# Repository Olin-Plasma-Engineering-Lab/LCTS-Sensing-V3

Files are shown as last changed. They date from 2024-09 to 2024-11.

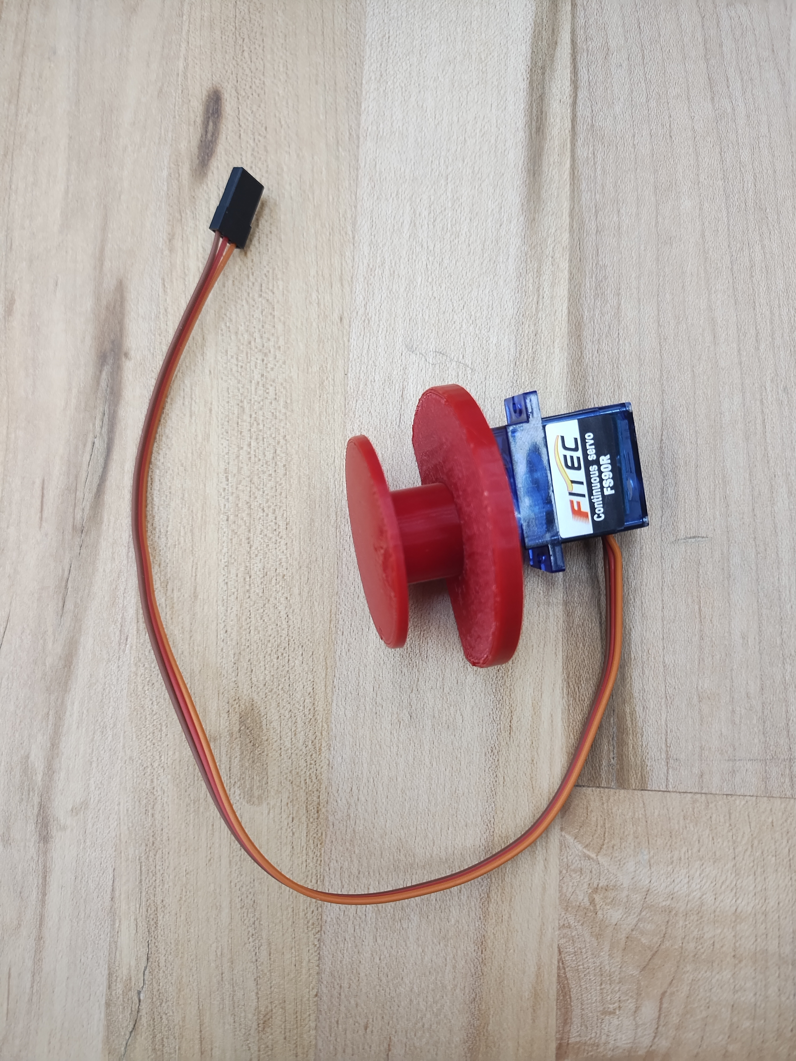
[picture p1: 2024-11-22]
assets/calibration servo.jpg

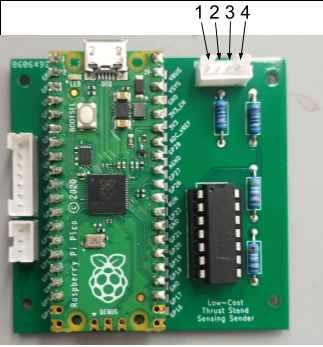
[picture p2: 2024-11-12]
assets/annotated force pinout sender.png

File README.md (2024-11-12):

# LCTS-Sensing-V3

This is the repository for the sensing system used by the Olin Plasma Engineering Lab (OPEL) to measure thrust on the Low-Cost Thrust Stand.

## Brief System Overview
The system is comprised of two boards: a sender and a receiver. The sender is located in the vacuum chamber and is connected to a force sensor that measures thrust produced by the thrusters. The receiver board is located outside the vacuum chamber and exists to receive data sent by the sender board. The boards are connected via a wiring harness and electrical feedthrough on the vacuum chamber, and communicate using I2C.

The system allows for two way communication. This gets used so that the calibration system on the thrust stand within the vacuum chamber can be controlled using the receiver board outside the chamber.

## Repository Organization

- `code/`: This contains the code used by the systems
    - `Microcontroller/`: Code that gets uploaded to the microcontrollers
        - `Arduino/`: Arduino code that gets uploaded to the microcontrollers
            - `receiver/`: code for the receiver board
            - `sender/` (depreicated): code for the sender board for use with **STEPPER MOTOR CALIBRATION**
            - `sender_servo_calibration/`: code for the sender board for use with **SERVO MOTOR CALIBRATION** This is the most up to date script and the code that is actually used on the sender board
        - `Micropython/`: Location for future microcontroller code written in MicroPython. Not currently used but contains the MicroPython firmware
- `Testing/`: Contain a Python script that was used as a preliminary test for saving data to a CSV
- `data/`: Data recorded from unlabeled thruster tests
- `Hardware/`: KiCad projects and other needed files for the sender and receiver PCBs
    - `assets/`: OPEL logo for use on PCBs
    - `Parts/`: Parts needed fro the KiCad Project files
    - `receiver/`: KiCad project files for the receiver PCB
    - `sender/`: KiCad project files for the sender PCB
- `sensing_processor.py`: Script that is used to read data from the receiver and save to a CSV
    
##

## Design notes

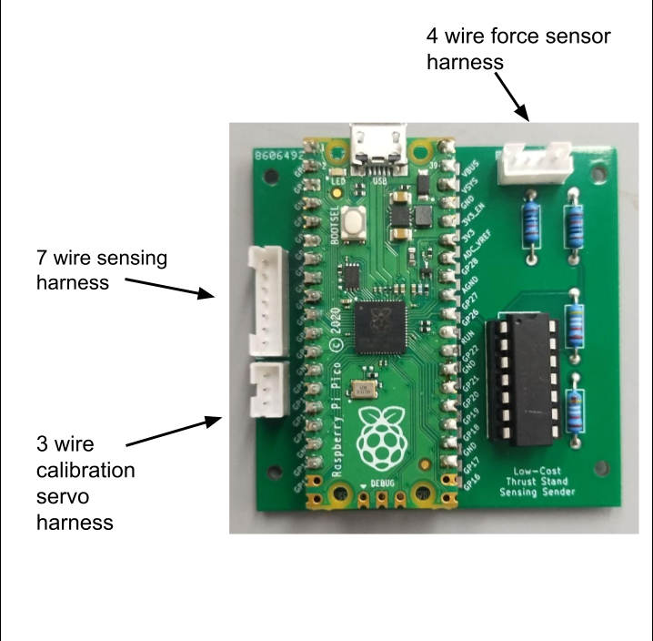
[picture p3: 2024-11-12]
assets/annotated_sender.png

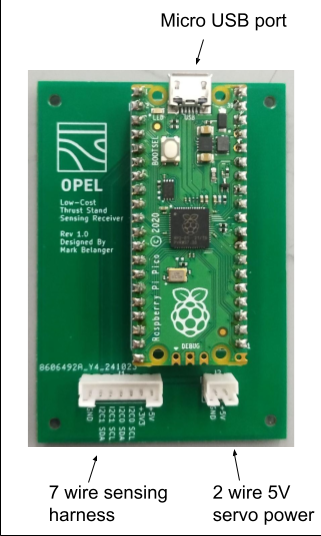
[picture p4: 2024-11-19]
assets/annotated harness receiver.png

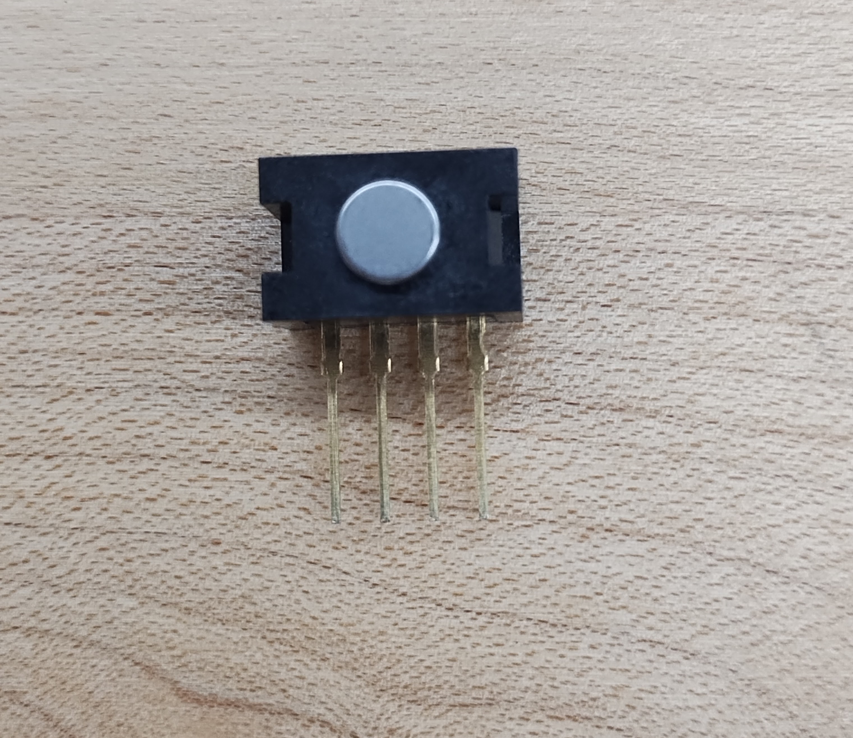
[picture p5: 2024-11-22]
assets/force sensor.jpg

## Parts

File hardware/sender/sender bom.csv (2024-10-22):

Id | Designator | Footprint | Quantity | Designation | Supplier and ref
1 | R2 | R_0603_1608Metric | 2 | 50k
2 | U3 | DIP254P762X508-14 | 1 | LMC6484IN_NOPB
3 | J1 | JST_PH_B7B-PH-K_1x07_P2.00mm_Vertical | 1 | Conn_01x07_Socket
4 | J3 | JST_PH_B3B-PH-K_1x03_P2.00mm_Vertical | 1 | Conn_01x03_Socket
5 | R1 | R_0603_1608Metric | 2 | 10k
6 | U4 | RPi_Pico_SMD_TH | 1 | Pico
7 | J2 | JST_PH_B4B-PH-K_1x04_P2.00mm_Vertical | 1 | Conn_01x04_Socket
8 | R4 | R_0603_1608Metric | 2 | 50k
9 | R3 | R_0603_1608Metric | 2 | 10k

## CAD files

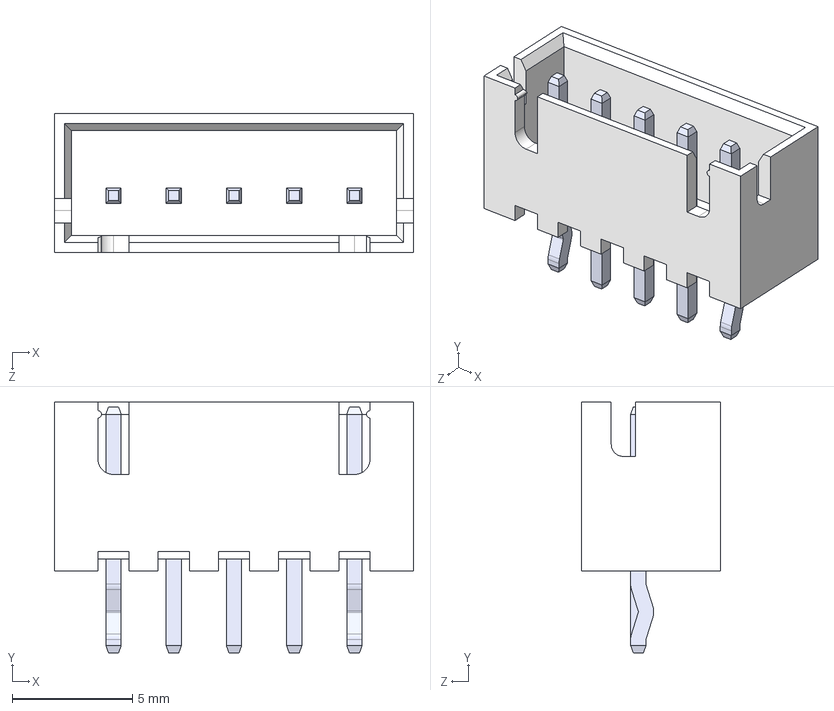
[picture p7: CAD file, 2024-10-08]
hardware/Parts/B5B_XH_A/B5B-XH-A.step
14.9 x 10.4 x 5.75 mm

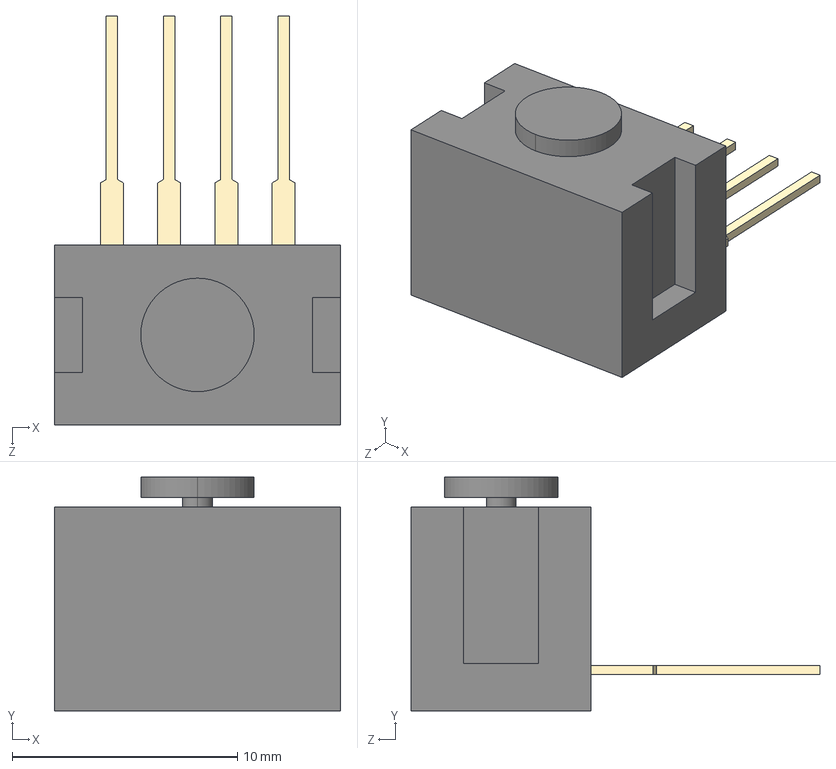
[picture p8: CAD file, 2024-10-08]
hardware/Parts/LIB_FSG005WNPB/3D/FSG005WNPB.stp
12.7 x 10.4 x 18.1 mm

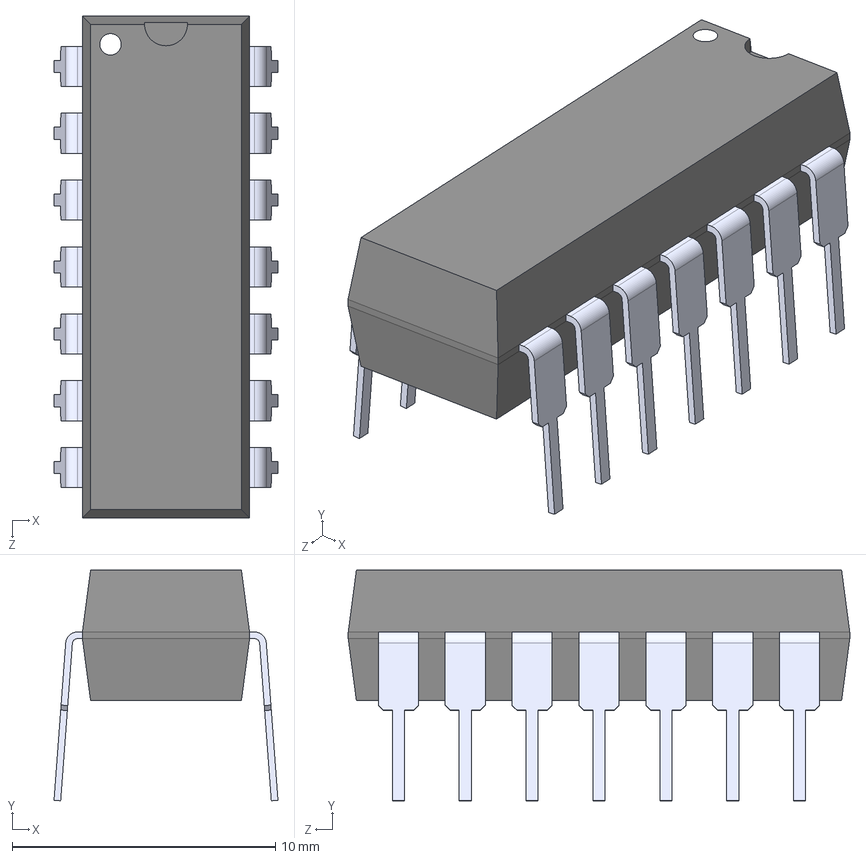
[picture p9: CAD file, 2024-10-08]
hardware/Parts/LMC6484IN_NOPB/LMC6484IN_NOPB.step
8.51 x 8.76 x 19.1 mm

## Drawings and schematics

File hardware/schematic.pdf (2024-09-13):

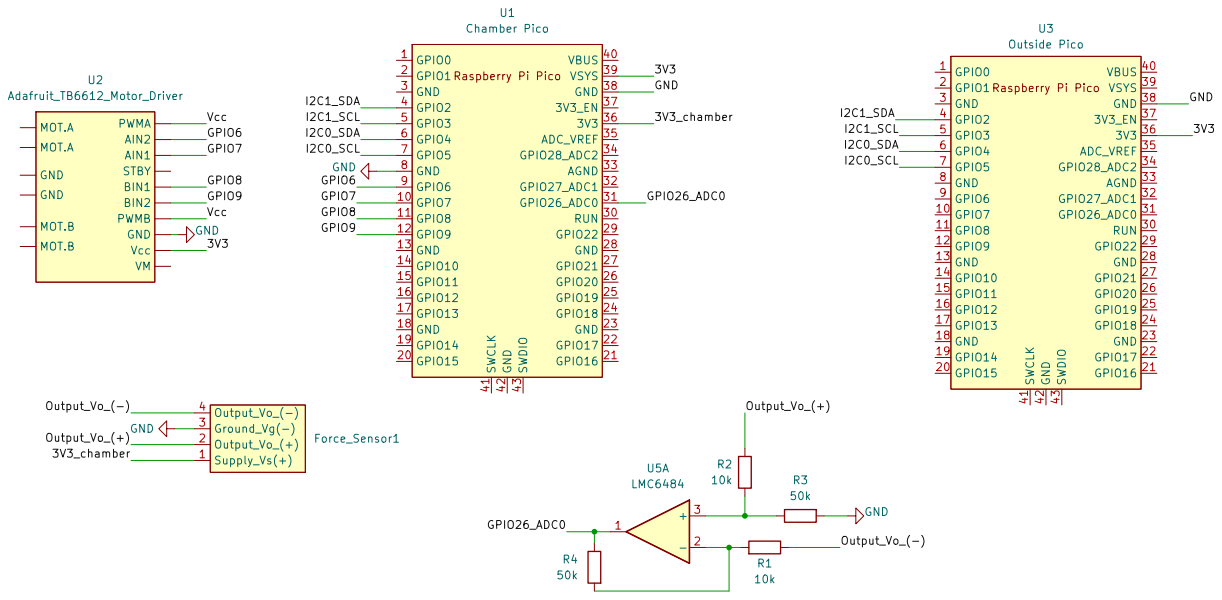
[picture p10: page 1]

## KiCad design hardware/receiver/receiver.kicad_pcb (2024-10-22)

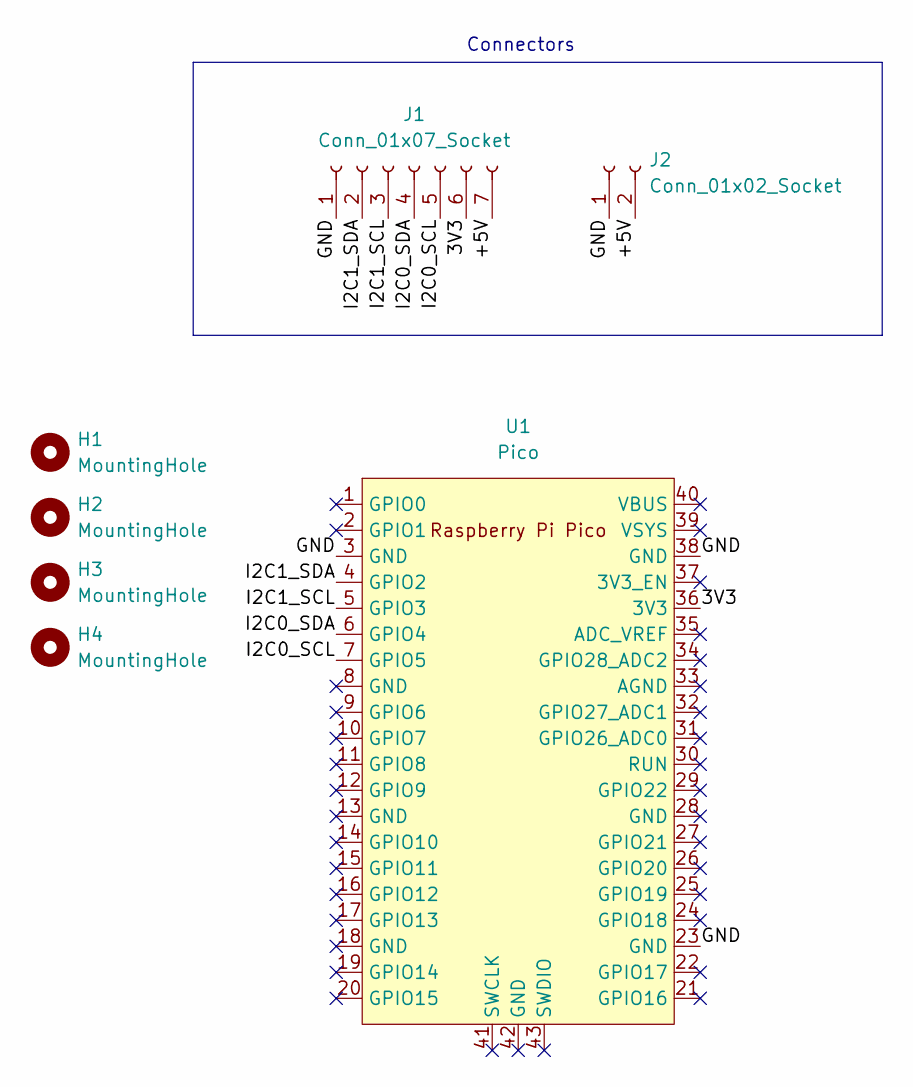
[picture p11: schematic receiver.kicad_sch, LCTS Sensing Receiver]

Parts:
H1, H2, H3, H4: MountingHole; MountingHole_2.2mm_M2
J1: Conn_01x07_Socket; JST_PH_B7B-PH-K_1x07_P2.00mm_Vertical
J2: Conn_01x02_Socket; JST_PH_B2B-PH-K_1x02_P2.00mm_Vertical
U1: Pico; RaspberryPi_Pico_Common_THT

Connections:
/3V3: J1.6, U1.36 (3V3)
/+5V: J1.7, J2.2
/GND: J1.1, J2.1, U1.3 (GND), U1.23 (GND), U1.38 (GND)
/I2C0_SCL: J1.5, U1.7 (GPIO5)
/I2C0_SDA: J1.4, U1.6 (GPIO4)
/I2C1_SCL: J1.3, U1.5 (GPIO3)
/I2C1_SDA: J1.2, U1.4 (GPIO2)

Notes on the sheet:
Connectors

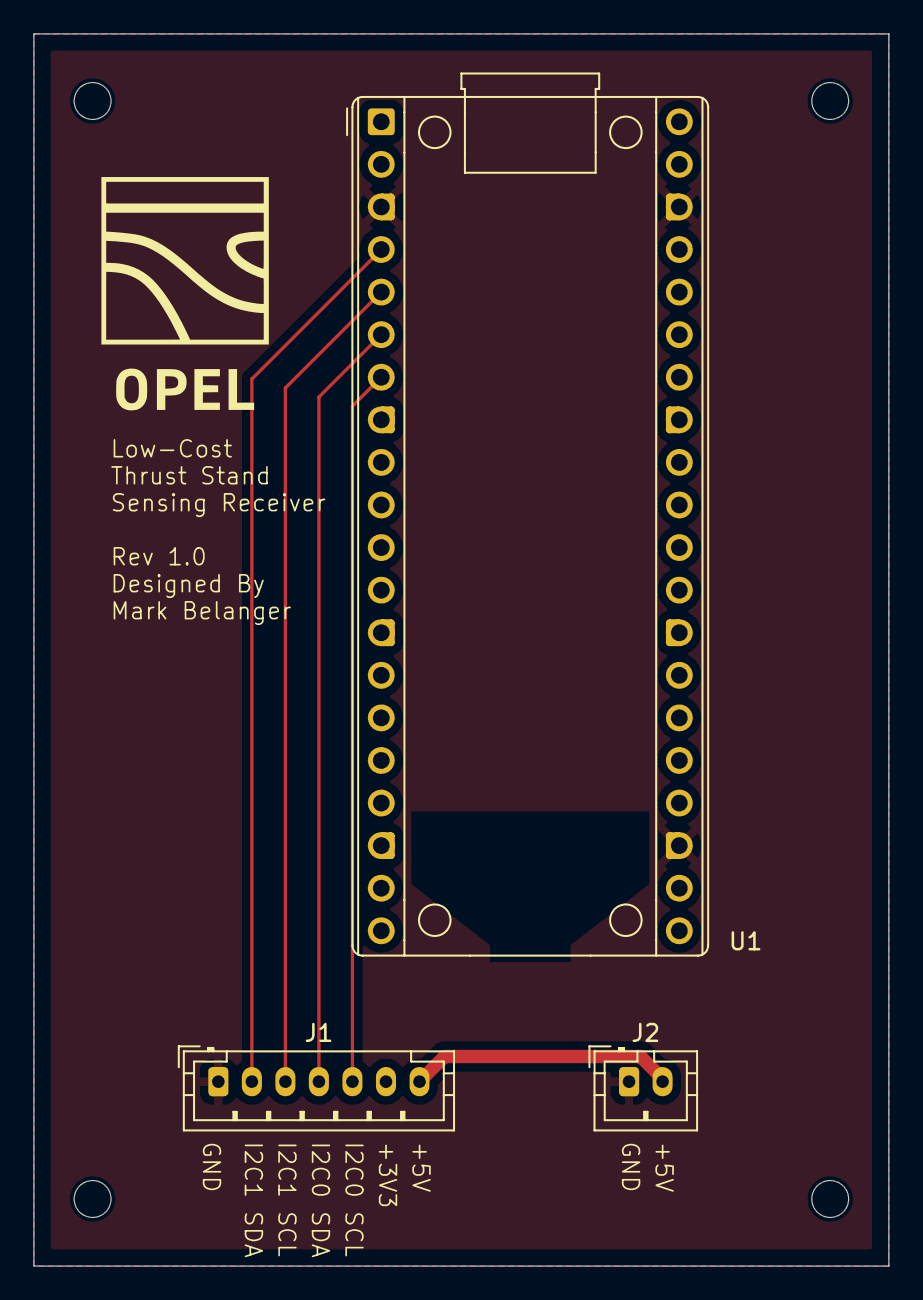
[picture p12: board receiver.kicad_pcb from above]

Board: 2 copper layers, 51.0 x 73.5 mm, 7 parts (0 on the bottom side), 7 nets.

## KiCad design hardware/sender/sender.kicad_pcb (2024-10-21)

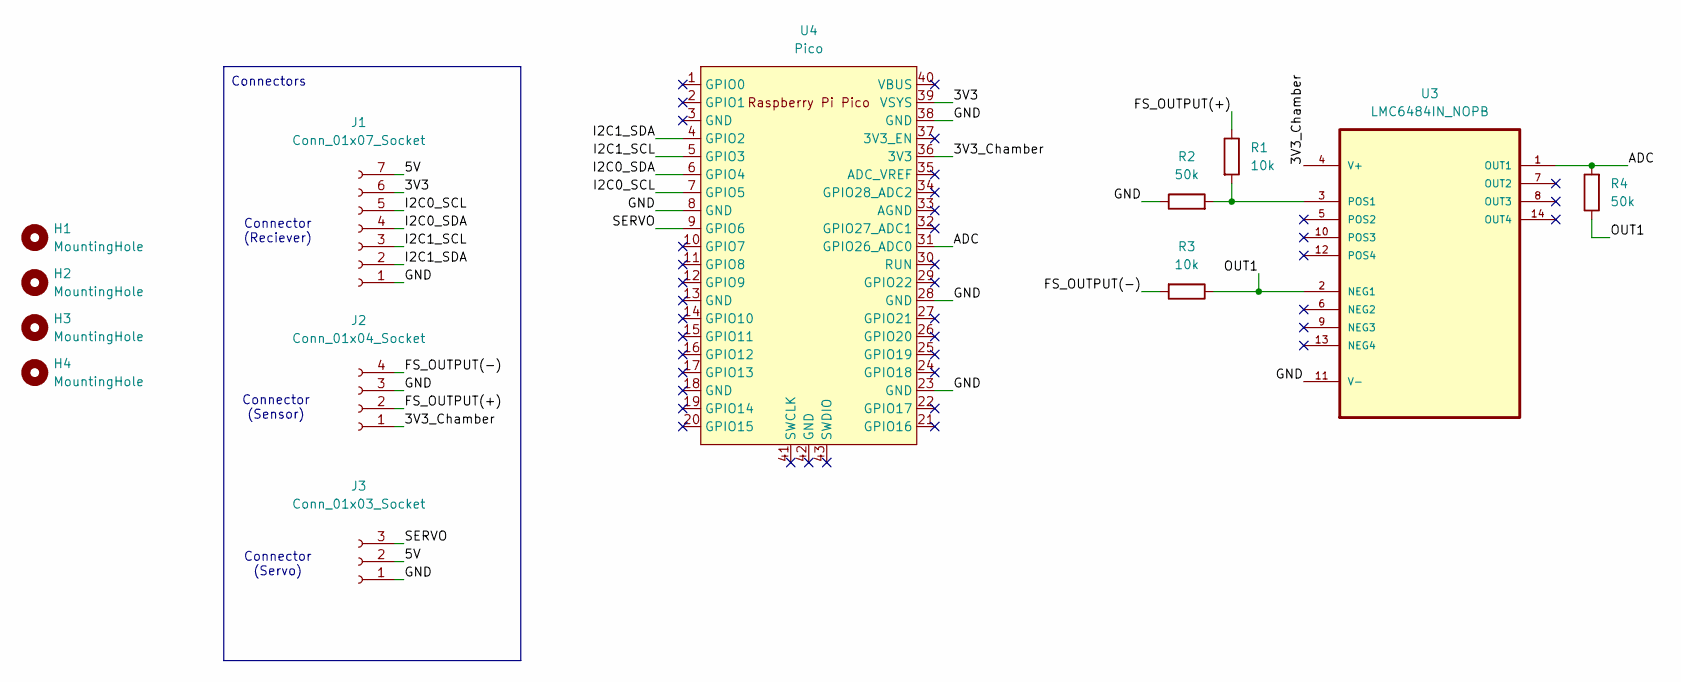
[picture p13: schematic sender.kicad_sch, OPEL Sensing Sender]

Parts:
H1, H2, H3, H4: MountingHole; MountingHole_2.2mm_M2
J1: Conn_01x07_Socket; JST_PH_B7B-PH-K_1x07_P2.00mm_Vertical
J2: Conn_01x04_Socket; JST_PH_B4B-PH-K_1x04_P2.00mm_Vertical
J3: Conn_01x03_Socket; JST_PH_B3B-PH-K_1x03_P2.00mm_Vertical
R1, R3: 10k; R_0603_1608Metric
R2, R4: 50k; R_0603_1608Metric
U3: LMC6484IN_NOPB; DIP254P762X508-14; MPN LMC6484IN/NOPB
U4: Pico; RPi_Pico_SMD_TH

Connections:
/3V3: J1.6, U4.39 (VSYS)
/3V3_Chamber: J2.1, U3.4 (V+), U4.36 (3V3)
/5V: J1.7, J3.2
/ADC: R4.2, U3.1 (OUT1), U4.31 (GPIO26_ADC0)
/FS_OUTPUT(+): J2.2, R1.1
/FS_OUTPUT(-): J2.4, R3.2
/GND: J1.1, J2.3, J3.1, R2.1, U3.11 (V-), U4.8 (GND), U4.23 (GND), U4.28 (GND), U4.38 (GND)
/I2C0_SCL: J1.5, U4.7 (GPIO5)
/I2C0_SDA: J1.4, U4.6 (GPIO4)
/I2C1_SCL: J1.3, U4.5 (GPIO3)
/I2C1_SDA: J1.2, U4.4 (GPIO2)
/OUT1: R3.1, R4.1, U3.2 (NEG1)
/SERVO: J3.3, U4.9 (GPIO6)
unnamed: R1.2, R2.2, U3.3 (POS1)

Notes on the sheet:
Connector (Servo)
Connector (Sensor)
Connectors
Connector (Reciever)

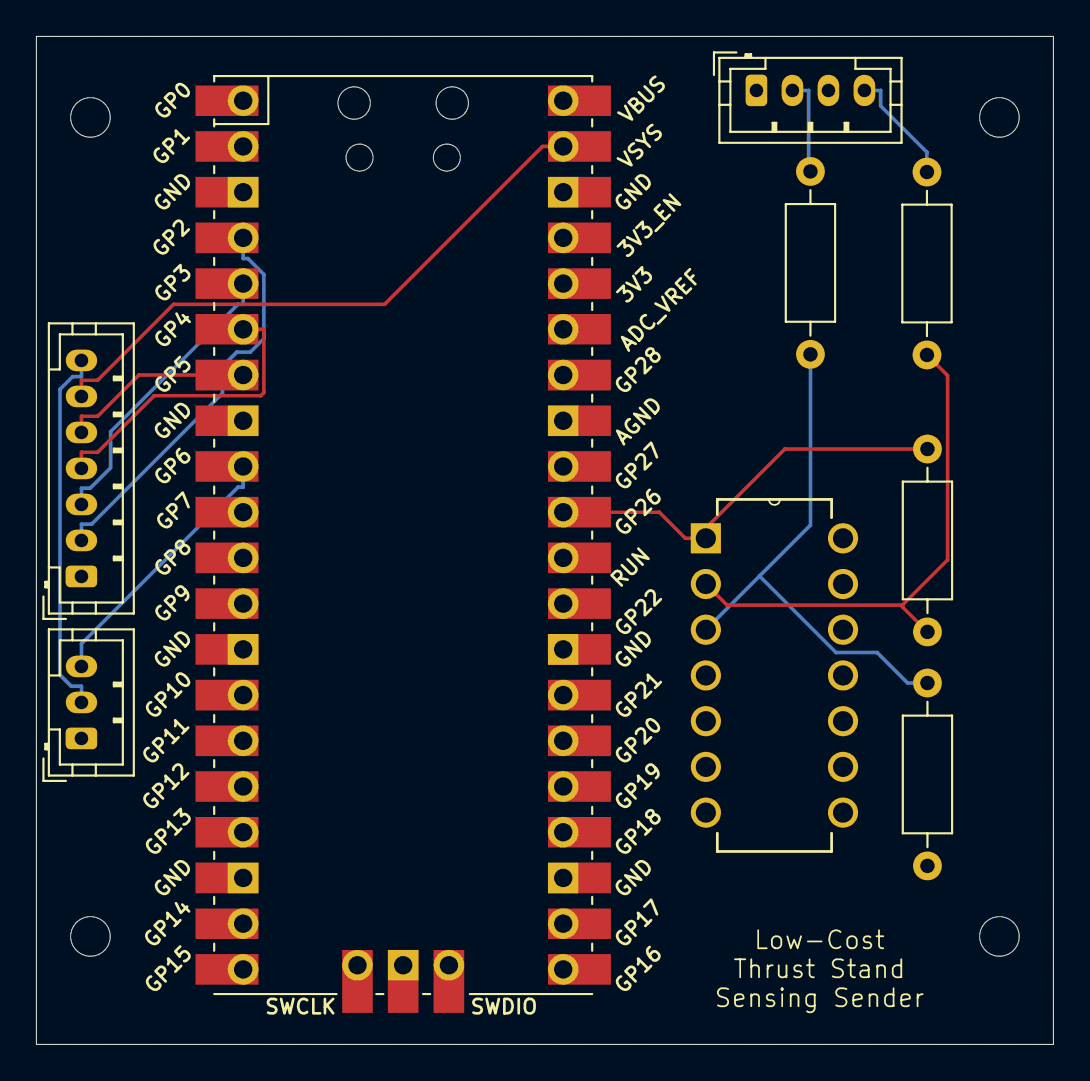
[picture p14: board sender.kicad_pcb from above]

Board: 2 copper layers, 56.5 x 56.0 mm, 14 parts (1 on the bottom side), 14 nets.

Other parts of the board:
G1: LOGO; opel_logo

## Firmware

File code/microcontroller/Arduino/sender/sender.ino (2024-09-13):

#include <Wire.h>
#include "Stepper.h"

int const COMMS_ADDR = 0x10;
int const CAL_ADDR = 0x20;
uint16_t force;
uint8_t FORCE_SENSOR = A0;
const int REVOLUTION_STEPS = 200;
uint16_t step = 200;

Stepper calibration(REVOLUTION_STEPS, 6, 7, 9, 8);

void setup()
{
  calibration.setSpeed(10);
  pinMode(FORCE_SENSOR, INPUT);
  pinMode(LED_BUILTIN, OUTPUT);
  digitalWrite(LED_BUILTIN, HIGH);
  Serial.begin(115200);
  Wire.begin();
  Wire1.setSDA(2);
  Wire1.setSCL(3);
  Wire1.begin(CAL_ADDR);
  Wire1.onReceive(receiveEvent);
}

void receiveEvent(int numBytes)
{
  byte direction = Wire1.read();
  Serial.println("Received");
  if (direction == 2)
  {
    calibration.step(step);
  }
  else if (direction == 1)
  {
    calibration.step(-step);
  }
  Serial.println(direction);
}

void loop()
{
  delay(50);
  force = analogRead(FORCE_SENSOR);

  // Split the 16-bit force value into two 8-bit values
  uint8_t msb = (force >> 8) & 0xFF;
  uint8_t lsb = force & 0xFF;

  Wire.beginTransmission(COMMS_ADDR);
  Wire.write(msb); // Send the most significant byte first
  Wire.write(lsb); // Send the least significant byte
  int result = Wire.endTransmission();

  // Debugging (if need be)

  if (result != 0)
  {
    Serial.print("Error in I2C transmission: ");
    Serial.println(result);
  }

  Serial.println(force);
}

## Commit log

2024-09-13 Add all content from V2 system
    [Trial 2024-04-17_14-48-11.csv, Trial 2024-04-17_15-34-42.csv]
2024-10-08 Add Sensing PCB KiCad Files
    [B5B-XH-A.step, FSG005WNPB.stp, LMC6484IN_NOPB.step, Sensing_PCB.kicad_pcb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]
2024-10-09 Add KiCad project for receiver PCB
    [Sensing_PCB.kicad_pcb, receiver.kicad_pcb, receiver.kicad_sch]
2024-10-10 Update receiver PCB
    Power and ground planes added
    Logo and title added to silkscreen
    [receiver.kicad_pcb, receiver.kicad_sch]
2024-10-10 Add Rev.1 of Sender PCB
    [Sensing_PCB.kicad_pcb, Sensing_PCB.kicad_sch]
2024-10-11 Update receiver PCB and add gerber files
    Added mounting holes, changes silk screen, and organized the schematic
    [receiver-B_Cu.gbr, receiver-B_Mask.gbr, receiver-B_Paste.gbr, receiver-B_Silkscreen.gbr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]
2024-10-11 Update Sender PCB
    [Sensing_PCB.kicad_pcb, Sensing_PCB.kicad_sch]
2024-10-21 New Sender Design
    [Sensing_PCB.kicad_pcb]
2024-10-22 Add gerber files to both boards
    BOM and footprint placement also added for sender board
    [Sensing_PCB-B_Cu.gbr, Sensing_PCB-B_Mask.gbr, Sensing_PCB-B_Paste.gbr, Sensing_PCB-B_Silkscreen.gbr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]
2024-11-19 Add annotated pic for receiver wiring harness
